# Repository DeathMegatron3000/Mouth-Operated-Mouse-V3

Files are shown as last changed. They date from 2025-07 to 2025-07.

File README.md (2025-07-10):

# Mouth-Operated Mouse V3

An open-source, affordable assistive technology project that enables computer control through mouth movements and sip/puff actions. This is an updated version of the original Mouth-Operated Mouse, now utilizing an Arduino Leonardo for direct HID (Human Interface Device) emulation and an enhanced Python application for calibration and training.

## Overview

This project creates a mouth-operated mouse combining a pressure sensor for sip/puff actions with a joystick for cursor movement, allowing users with limited hand mobility to control a computer. A keyboard mode is also included, where 2 to 8 keybinds are assigned to different angles, and special keys can be binded to sips and puffs. The device functions as follows:

*   **Joystick**: Controls cursor movement (operated by mouth)
*   **Sip/Puff Actions**:
    *   Hard sip → Right click
    *   Soft sip → Scroll down
    *   Neutral → No action
    *   Soft puff → Scroll up
    *   Hard puff → Left click

## Key Features of V3

*   **Arduino Leonardo Integration**: Direct USB HID emulation, eliminating the need for a separate Python script for mouse control on the computer side. The Arduino Leonardo can act directly as a mouse.
*   **Enhanced Python Application (`App.py`)**: A comprehensive GUI application built with `customtkinter` for:
    *   **Tuning & Profiles**: Adjust pressure thresholds and joystick sensitivity, save and load custom profiles.
    *   **Trainer**: Interactive exercises to improve sip/puff and joystick control accuracy.
    *   **Calibrate Sensor**: Visualize real-time pressure data and assist in setting optimal thresholds.
    *   **Stick Control**: Visual representation of joystick input and deadzone.

*   **Improved Responsiveness**: Direct HID communication from Arduino Leonardo offers lower latency.
*   **Modular Design**: Easy customization and integration of components.

## Components

1.  **Arduino pro micro** (~$1.53 AUD)
    *   Replaces Arduino Uno and Leonardo for direct HID capabilities and a more compact design.
2.  **NPA-300B-001G (Most NPA pressure sensor models will work)** (~$2.8 to 54 AUD)
    *    - Specifically designed for sip/puff applications
         - Note that most models operated imilarly, meaning that there is no point in buying the more expensive models of the NPA sensors
3.  **Joystick Module**
    *   Analog Thumb Joystick Module (~$0.35 AUD)
4.  **Tubing and Mouthpiece:**
    *   Food-grade silicone tubing 1 meter - 2mm x 3mm (~$1.39 AUD) 
5.  **3d Printed parts**
    *   Mouthpeice, Casing, and arm (Cost varies, but estimated around 35 AUD)
5.  **Soldering Components:**
    *   3cm x 7cm proto board (~$0.14 AUD)
    *   Basic soldering stuff, wires, solder, flux (Cost varies, estimated around 2 to 3 AUD for me)
    *   USB to USB-C cable for Arduino (~$0.73 AUD)
    *   1 micro farad capacitor (~$0.16 AUD)
    *   DIP14 PCB Adapter Plate (~$0.55 AUD)
    
**Estimated Total Cost:** Approximately $45 AUD not including shipping, cost varies from country to country

## Setup Instructions

### 1. Hardware Assembly

Follow these basic instructions:

*   **Pressure Sensor (NPA-300B-001G) Connections:**
    *   VSS/Pin 6  → Arduino GND and VDD/Pin 9 through a 1 microfarad capacitor
    *   VDD/Pin 9  → Arduino +2.7 to +5.5V
    *   SIG/Pin 8 → Arduino A0
*   **Joystick Module Connections:**
    *   GND pin → Arduino GND 
    *   +5V pin → Arduino 5V (Connect with the Pressure sensor VDD/Pin 9 connection)
    *   VRx (X-axis) → Arduino A1
    *   VRy (Y-axis) → Arduino A2
    *   SW (Switch, optional) → Not used, but can be connected to a digital pin if desired
*   **Tubing Connection:**
    *   Connect silicon food-grade tubing to the pressure port on the sensor, there are 2 pressure ports for most models, the one further away from the dot in the corner should be the one you connect to, the other one inverts sips and puffs
    *   Thread your tubing through the hole on top of the casing
    *   Connect your mouthpiece to the joystick shaft
    *   The other end of the tubing connects to the hole on the mouthpiece, make sure the hole on the mouthpeice is facing upwards
*   **Casing** 
    *   Make sure everything works first, and that the joystick has enough angle of movement
    *   Assemble the 3d printed arm/stand (link at the bottom of this file) with the final screw connecting the casing with the 3d printed arm/stand
    *   Once everything works, connect your cable to the arduino, and slide the cover over the open side of the casing

*   **Tips and advices**
    *   Depending on your 3d printer settings, some of the components might not fit, simply sand down the parts that are too big or too tight, such as the thin part of the sliding cover, or the screw and screw hole, DO NOT SAND DOWN yOUR MOUTHPEICE, you do not want to breathe in the fiament dust, if the hole does not fit on the hatch, you can use a small screwdriver and apply force to the hole and expand it a bit.
    *   Some model of the sensors, such as the one used for this project (NPA-300B-001G) has an uneven pressure detection range, meaning that it can detect stronger puffs and weaker sips, this can cause the sips to be very sensitive, so much so that it is very difficult to control the soft and hard sips, to fix this, simple poke a few holes in the tubing
    *   Remember to connect capacitor with correct polarity if you are using an electrolytic capacitor

### 2. Arduino IDE Setup

1.  **Install Arduino IDE**: Download and install the Arduino IDE from the [official website](https://www.arduino.cc/en/software).
2.  **Install Arduino Pro Micro Board**: Go to `Tools > Board > Boards Manager...` and search for "Arduino AVR Boards". Install the package that includes the Arduino Leonardo.
3.  **Install Libraries**: The `V3.ino` sketch uses the built-in `Mouse.h` library. No additional library installations are required for the Arduino sketch.
4.  **Upload Sketch**: Open `V3.ino` in the Arduino IDE, select `Tools > Board > Arduino Pro Micro`, and choose the correct `Port`. Then, click `Upload`.

### 3. Python Application Setup

1.  **Install Python**: Ensure you have Python 3.x installed. You can download it from [python.org](https://www.python.org/downloads/).
2.  **Install Dependencies**: Open a terminal or command prompt and navigate to the directory where `App.py` is located. Install the required Python libraries using pip:
    ```bash
    pip install pyserial customtkinter pyautogui
    ```
3.  **Run Application**: Execute the Python application:
    ```bash
    python App.py
    ```

## Usage

Once the Arduino sketch is uploaded and the Python application is running, you can use the `App.py` interface to:

*   **Connect to Arduino**: Select the serial port connected to your Arduino Leonardo and click "Connect".
*   **Tune Parameters**: Adjust the pressure thresholds (Hard Sip, Neutral Min/Max, Soft Puff, Hard Puff) and joystick deadzone/cursor speed. Apply settings to the Arduino.
*   **Calibrate Sensor**: Use the "Calibrate Sensor" tab to visualize real-time pressure readings and fine-tune your thresholds for optimal performance.
*   **Train**: Utilize the "Trainer" tab to practice and improve your control.
*   **Manage Profiles**: Save and load different configurations as profiles.

## Troubleshooting

*   **Arduino Not Detected**: Ensure the Arduino Pro Micro drivers are correctly installed and the correct port is selected in the Arduino IDE and `App.py`.
*   **Serial Communication Issues**: Verify that no other application is using the serial port. Restarting the Arduino IDE or `App.py` might help.
*   **Mouse Not Moving/Clicking**: Check the pressure sensor and joystick connections. Ensure the `V3.ino` sketch is successfully uploaded to the Arduino Leonardo.
*   **Calibration**: The pressure thresholds are highly dependent on your specific sensor and lung capacity. Use the "Calibrate Sensor" tab in `App.py` to find your optimal settings.

## Link for 3d printed arm/stand: https://www.printables.com/model/647794-flexible-sturdy-phone-arm-100-printed/files

*  **There is no need to print the CZFA_FlexFrame_PhoneMount.stl, as that is a phone stand, instead, you are connecting the screw that was suppose to join the phone holder and the arm/stand to the casing instead

## Link for video guides:

* Hardware: https://youtu.be/UBpAdc31Nfw
* Software: https://youtu.be/A-l-xfMGubU

## 🛠️ OSHWA Certification

This hardware project is certified by the [Open Source Hardware Association (OSHWA)](https://www.oshwa.org/).

**Certification UID**: [AU000021](https://certification.oshwa.org/au000021.html)
## Contributing

Contributions are welcome! Please feel free to fork the repository, make improvements, and submit pull requests. For major changes, please open an issue first to discuss what you would like to change.

## License

This project is open-source and available under the [MIT License](https://opensource.org/licenses/MIT).

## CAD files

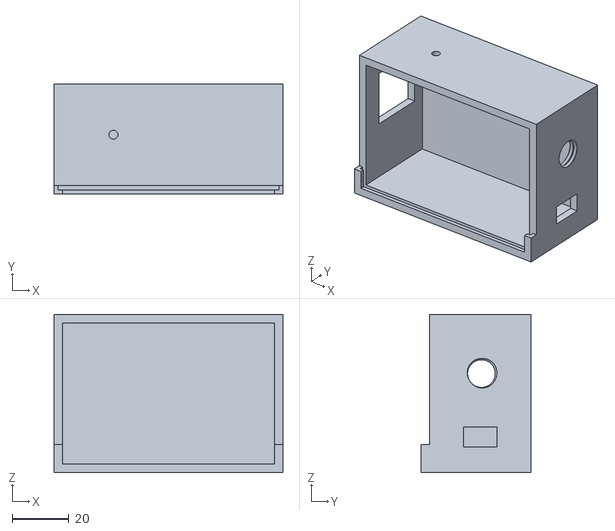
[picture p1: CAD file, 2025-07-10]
Case.stl
81.0 x 39.0 x 56.0

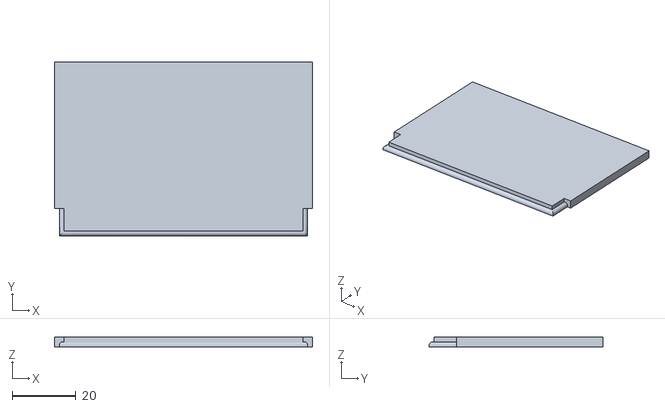
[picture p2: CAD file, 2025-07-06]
Case cover.stl
81.0 x 54.5 x 3.00

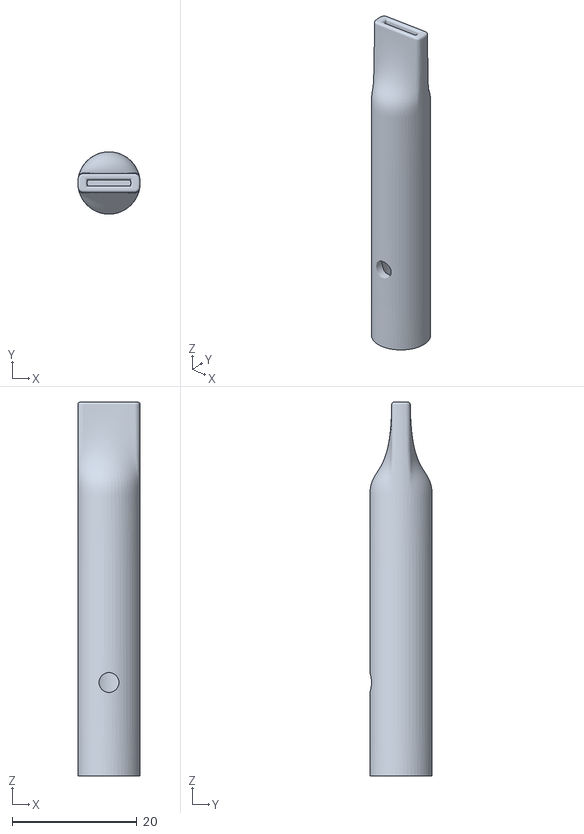
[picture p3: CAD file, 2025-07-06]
mouthpiece.stl
10.0 x 10.00 x 60.0

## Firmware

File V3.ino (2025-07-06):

// =================================================================
// Integrated Hybrid Controller Sketch - FINAL & COMPLETE
// =================================================================

#include <Mouse.h>
#include <Keyboard.h>
#include <math.h>

// --- Pin Definitions ---
const int PRESSURE_PIN = A0;
const int JOY_X_PIN = A1;
const int JOY_Y_PIN = A2;

// --- Operating Modes ---
#define MODE_MOUSE 0
#define MODE_KEYBOARD 1
byte currentMode = MODE_MOUSE;

// --- State Flags ---
bool isLeftPressed_mouse = false;
bool isRightPressed_mouse = false;
bool isHardSipKeyHeld_kbd = false;
bool isSoftSipKeyHeld_kbd = false;
bool isSoftPuffKeyHeld_kbd = false;
bool isHardPuffKeyHeld_kbd = false;
int last_pressed_joy_key_index = -1;

// --- Parameters (Set by the Python GUI) ---
int hardSipThreshold = -200;
int neutralMin = -100;
int neutralMax = 25;
int softPuffThreshold = 100;
int hardPuffThreshold = 200;
int joystickDeadzone = 20;
int joystickMovementThreshold = 10;
int cursorSpeed = 10;
int softActionDelay = 150;

int sipSensitivity = 100;
int puffSensitivity = 100;

// --- CUSTOMIZABLE KEYBOARD VARS ---
int num_joy_sections = 8;
// *** NEW: Store two keys per sector ***
byte joy_keybinds[16][2]; // [sector_index][key_index: 0 or 1]
byte key_hpt = 'f';
byte key_spt = 'r';
byte key_hst = 'e';
byte key_sst = 'q';

// --- Timing, Sampling & Calibration ---
unsigned long sampleTimer = 0;
const int SAMPLE_PERIOD_MS = 5;
const int SAMPLE_LENGTH = 10;
int pressureSamples[SAMPLE_LENGTH];
int sampleCounter = 0;
unsigned long inputUpdateTimer = 0;
const int INPUT_UPDATE_PERIOD_MS = 15;
bool calibrationModeActive = false;
unsigned long lastCalibSendTime = 0;
int joyXCenter, joyYCenter;
int pressureCenter;

void setup() {
  Serial.begin(115200);

  Mouse.begin();
  Keyboard.begin();
  
  delay(1000); 
  
  long pressureSum = 0;
  for (int i = 0; i < 32; i++) {
    pressureSum += analogRead(PRESSURE_PIN);
    delay(10); 
  }
  pressureCenter = pressureSum / 32;
  
  joyXCenter = analogRead(JOY_X_PIN);
  joyYCenter = analogRead(JOY_Y_PIN);
  
  // Set default keybinds (now with two keys)
  char default_keys[8][2] = {{'d', ' '}, {'d', 's'}, {'s', ' '}, {'a', 's'}, {'a', ' '}, {'a', 'w'}, {'w', ' '}, {'w', 'd'}};
  for(int i = 0; i < 8; i++){
    joy_keybinds[i][0] = default_keys[i][0];
    joy_keybinds[i][1] = default_keys[i][1];
  }
  
  releaseAllInputs();
  Serial.print("INFO:Calibrated Pressure Center: ");
  Serial.println(pressureCenter);
  Serial.println("INFO:Controller Ready. Default Mode: Mouse");
}

void loop() {
  handleSerialCommands();

  if (calibrationModeActive) {
    if (millis() - lastCalibSendTime >= 50) {
      int raw_pressure = analogRead(PRESSURE_PIN) - pressureCenter;
      int scaled_pressure;
      if (raw_pressure < 0) {
        scaled_pressure = (long)raw_pressure * sipSensitivity / 100;
      } else {
        scaled_pressure = (long)raw_pressure * puffSensitivity / 100;
      }
      Serial.print("CALIB_P:");
      Serial.println(scaled_pressure);
      lastCalibSendTime = millis();
    }
    return;
  }

  if (millis() - sampleTimer >= SAMPLE_PERIOD_MS) {
    samplePressure();
    sampleTimer = millis();
  }
  
  if (currentMode == MODE_MOUSE) {
    if (sampleCounter >= SAMPLE_LENGTH) {
      int avgPressure = calculateAveragePressure();
      Serial.print("P:"); Serial.println(avgPressure);
      processPressureMouse(avgPressure);
      sampleCounter = 0; 
    }
    if (millis() - inputUpdateTimer >= INPUT_UPDATE_PERIOD_MS) {
      updateMouseJoystick();
      inputUpdateTimer = millis();
    }
  } else if (currentMode == MODE_KEYBOARD) {
    if (sampleCounter >= SAMPLE_LENGTH) {
      int avgPressure = calculateAveragePressure();
      Serial.print("P:"); Serial.println(avgPressure);
      processPressureKeyboard(avgPressure);
      sampleCounter = 0;
    }
    if (millis() - inputUpdateTimer >= INPUT_UPDATE_PERIOD_MS) {
      updateKeyboardJoystick();
      inputUpdateTimer = millis();
    }
  }
}

// =================================================================
// SENSOR & INPUT PROCESSING
// =================================================================
void samplePressure() {
  if (sampleCounter < SAMPLE_LENGTH) {
    int raw_centered_pressure = analogRead(PRESSURE_PIN) - pressureCenter;
    
    int scaled_pressure;
    if (raw_centered_pressure < 0) {
      scaled_pressure = (long)raw_centered_pressure * sipSensitivity / 100;
    } else {
      scaled_pressure = (long)raw_centered_pressure * puffSensitivity / 100;
    }
    
    pressureSamples[sampleCounter] = scaled_pressure;
    sampleCounter++;
  }
}

int calculateAveragePressure() {
  long sum = 0;
  for (int i = 0; i < SAMPLE_LENGTH; i++) sum += pressureSamples[i];
  return sum / SAMPLE_LENGTH;
}

void processPressureMouse(int pressure) {
  if (pressure >= hardPuffThreshold) { if (!isLeftPressed_mouse) { Mouse.press(MOUSE_LEFT); isLeftPressed_mouse = true; } } 
  else { if (isLeftPressed_mouse) { Mouse.release(MOUSE_LEFT); isLeftPressed_mouse = false; } }
  
  if (pressure <= hardSipThreshold) { if (!isRightPressed_mouse) { Mouse.press(MOUSE_RIGHT); isRightPressed_mouse = true; } }
  else { if (isRightPressed_mouse) { Mouse.release(MOUSE_RIGHT); isRightPressed_mouse = false; } }

  if (pressure >= softPuffThreshold && pressure < hardPuffThreshold) { Mouse.move(0, 0, 1); } 
  else if (pressure <= neutralMin && pressure > hardSipThreshold) { Mouse.move(0, 0, -1); }
}

void processPressureKeyboard(int pressure) {
  if (pressure >= hardPuffThreshold) { if (!isHardPuffKeyHeld_kbd) { Keyboard.press(key_hpt); isHardPuffKeyHeld_kbd = true; } } 
  else { if (isHardPuffKeyHeld_kbd) { Keyboard.release(key_hpt); isHardPuffKeyHeld_kbd = false; } }
  
  if (pressure >= softPuffThreshold && pressure < hardPuffThreshold) { if (!isSoftPuffKeyHeld_kbd) { Keyboard.press(key_spt); isSoftPuffKeyHeld_kbd = true; } }
  else { if (isSoftPuffKeyHeld_kbd) { Keyboard.release(key_spt); isSoftPuffKeyHeld_kbd = false; } }

  if (pressure <= hardSipThreshold) { if (!isHardSipKeyHeld_kbd) { Keyboard.press(key_hst); isHardSipKeyHeld_kbd = true; } }
  else { if (isHardSipKeyHeld_kbd) { Keyboard.release(key_hst); isHardSipKeyHeld_kbd = false; } }
  
  if (pressure <= neutralMin && pressure > hardSipThreshold) { if (!isSoftSipKeyHeld_kbd) { Keyboard.press(key_sst); isSoftSipKeyHeld_kbd = true; } }
  else { if (isSoftSipKeyHeld_kbd) { Keyboard.release(key_sst); isSoftSipKeyHeld_kbd = false; } }
}

void updateKeyboardJoystick() {
  int joyX = analogRead(JOY_X_PIN) - joyXCenter;
  int joyY = analogRead(JOY_Y_PIN) - joyYCenter;
  Serial.print("JOY:"); Serial.print(joyX); Serial.print(","); Serial.println(joyY);

  float magnitude = sqrt(pow(joyX, 2) + pow(joyY, 2));
  int current_section_index = -1;
  
  if ((magnitude / 512.0) * 100.0 > joystickMovementThreshold) {
      float slice_angle = 360.0 / num_joy_sections;
      float angle = atan2((float)-joyY, (float)joyX) * 180.0 / PI; 
      
      angle += slice_angle / 2.0;
      if (angle < 0) { angle += 360.0; }
      if (angle >= 360.0) { angle -= 360.0; }
      
      current_section_index = floor(angle / slice_angle);
  }

  if (current_section_index != last_pressed_joy_key_index) {
    // Release the previously held keys
    if (last_pressed_joy_key_index != -1) { 
      if(joy_keybinds[last_pressed_joy_key_index][0] != ' ') Keyboard.release(joy_keybinds[last_pressed_joy_key_index][0]);
      if(joy_keybinds[last_pressed_joy_key_index][1] != ' ') Keyboard.release(joy_keybinds[last_pressed_joy_key_index][1]);
    }
    // Press the new keys (if any)
    if (current_section_index != -1) { 
      if(joy_keybinds[current_section_index][0] != ' ') Keyboard.press(joy_keybinds[current_section_index][0]);
      if(joy_keybinds[current_section_index][1] != ' ') Keyboard.press(joy_keybinds[current_section_index][1]);
    }
    last_pressed_joy_key_index = current_section_index;
  }
}

void updateMouseJoystick() {
  int joyX = analogRead(JOY_X_PIN) - joyXCenter;
  int joyY = analogRead(JOY_Y_PIN) - joyYCenter;
  Serial.print("JOY:"); Serial.print(joyX); Serial.print(","); Serial.println(joyY);
  
  float xPercent = (float)joyX / 512.0 * 100.0;
  float yPercent = (float)joyY / 512.0 * 100.0;
  int moveX = 0, moveY = 0;

  if (abs(xPercent) > joystickDeadzone) {
    moveX = map(xPercent, (xPercent > 0 ? joystickDeadzone : -100), (xPercent > 0 ? 100 : -joystickDeadzone), (xPercent > 0 ? 1 : -cursorSpeed), (xPercent > 0 ? cursorSpeed : -1));
  }
  if (abs(yPercent) > joystickDeadzone) {
    moveY = -map(yPercent, (yPercent > 0 ? joystickDeadzone : -100), (yPercent > 0 ? 100 : -joystickDeadzone), (yPercent > 0 ? 1 : -cursorSpeed), (yPercent > 0 ? cursorSpeed : -1));
  }
  
  if (moveX != 0 || moveY != 0) {
    Mouse.move(moveX, moveY, 0);
  }
}

// =================================================================
// SERIAL COMMANDS & STATE MANAGEMENT
// =================================================================
void releaseAllInputs() {
  Mouse.release(MOUSE_LEFT); Mouse.release(MOUSE_RIGHT); Keyboard.releaseAll();
  isLeftPressed_mouse = false; isRightPressed_mouse = false;
  isHardSipKeyHeld_kbd = false; isSoftSipKeyHeld_kbd = false; isSoftPuffKeyHeld_kbd = false; isHardPuffKeyHeld_kbd = false;
  
  if (last_pressed_joy_key_index != -1) {
    if(joy_keybinds[last_pressed_joy_key_index][0] != ' ') Keyboard.release(joy_keybinds[last_pressed_joy_key_index][0]);
    if(joy_keybinds[last_pressed_joy_key_index][1] != ' ') Keyboard.release(joy_keybinds[last_pressed_joy_key_index][1]);
    last_pressed_joy_key_index = -1;
  }
}
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
